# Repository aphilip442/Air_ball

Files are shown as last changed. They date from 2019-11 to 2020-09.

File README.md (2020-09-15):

# Air_ball

Describes how to make a 3D printed air ball holder with mouse sensors to capture the ball's motion. 

Can be used in behavioral rigs with mice.

Demo CountPages airball (https://www.youtube.com/watch?v=CR8DfGOpQPQ)

## Parts

* 3D printed parts: bottom and top
* M6 thread heat-insert: https://befr.rs-online.com/web/p/threaded-inserts/0278629/
* M4 thread heat-insert: https://befr.rs-online.com/web/p/threaded-inserts/0278607/
* M6 pneumatic push-in fitting: https://befr.rs-online.com/web/p/pneumatic-straight-fittings/1216041/
* Pressure regulator : SMC pneumatics - Model: ARM11A B3-208-J1: 
https://www.smc.eu/portal_ssl/WebContent/digital_catalog_2/jsp/view_product_configurator.jsp?dc_product_id=87018&part_number=ARM11AB3-508-J1
* 6mm tubing: https://www.smc.eu/portal_ssl/WebContent/digital_catalog_2/jsp/view_product_configurator.jsp?dc_product_id=54694&lang=fr&ctry=BE
* Warning: this assumes you have a source for pressured air

## How to assemble

* 3D print the components (black PLA)
* Heat-insert M4-M6 threads in the 3D parts with a soldering iron
* Put an M6 push-in fitting in the only hole that goes through the plastic
* Use epoxy to glue bottom and top parts

# Motion Sensors 
## Parts

* 2x 3D printed parts: sensor holder 
* 2x Motion sensor PMW3360: https://www.tindie.com/products/jkicklighter/pmw3360-motion-sensor/
* 2x Arduino Micro
* 1x Arduino Due
* 1x PCB

## Power

Both board types take 12V on Vin and share the same GND.

## How to connect sensors to Micros

Pinout Sensor - Micro:
-------
* RS --- (NONE)
* GD --- GND
* MT --- Pin 7 (PE6, INT6) -> movement interrupt
* SS --- Pin 10 (PB6)
* SC --- SCK (PB1)
* MO --- MOSI (PB2)
* MI --- MISO (PB3)
* VI --- 5V

https://www.tindie.com/products/jkicklighter/pmw3360-motion-sensor/

## How to connect Micros to Due

We are using the serial ports and the Due provides power.

WARNING: the Due works on 3.3V and the Micros on 5V.

Pinout Due - Micro
-------
* RX  = voltage divider from TX (5V(micro)->3.3V(due), use 2k and 1k resistors)

# Micro's output

XY motion from the sensor, sampled at around 1kHz

# Due's output

Yaw - pitch - roll values (you can add eventual other outputs like the total distance)

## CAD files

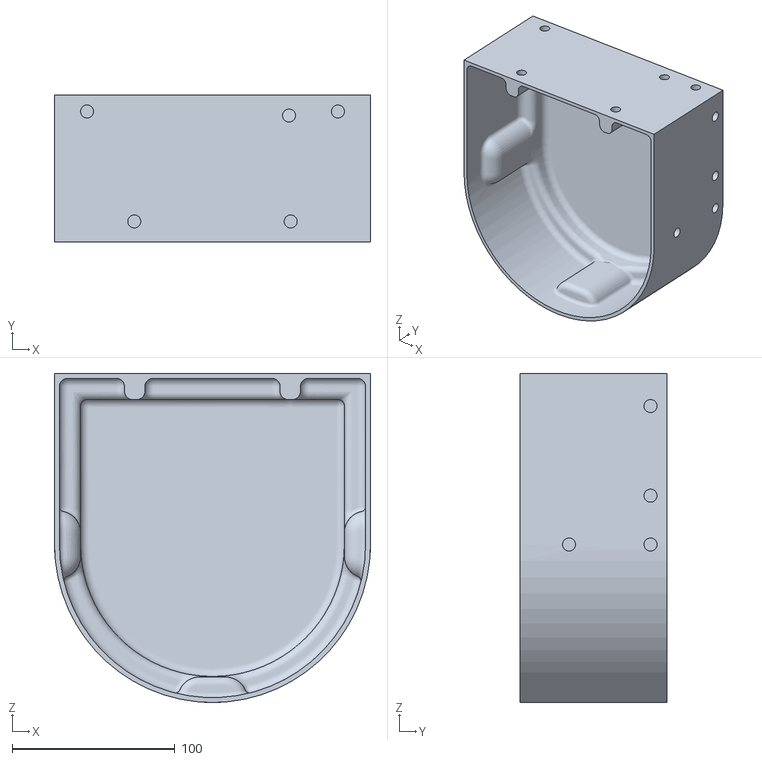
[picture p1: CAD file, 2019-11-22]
cad_files/air_ball_bottom.STL
194.0 x 90.0 x 202.0

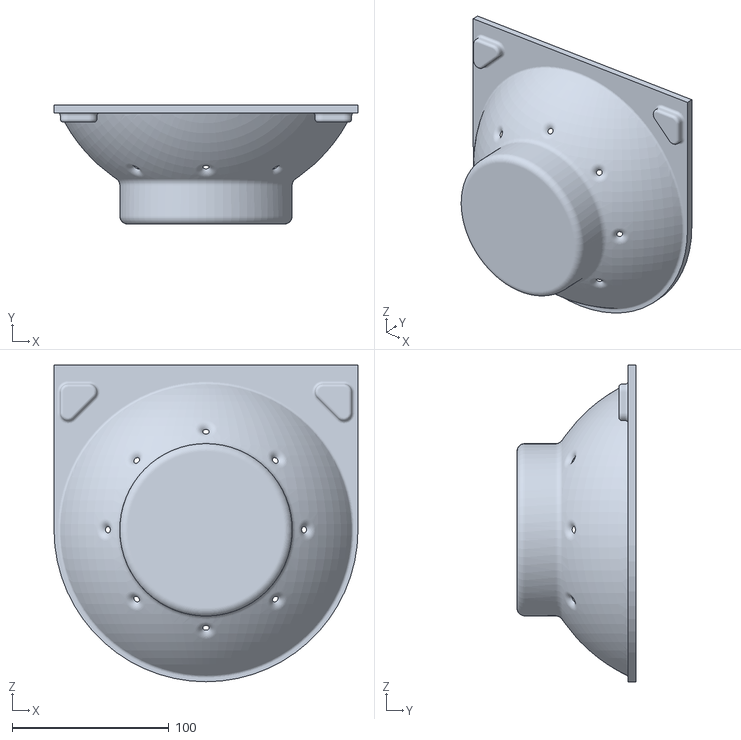
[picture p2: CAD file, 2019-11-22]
cad_files/air_ball_top.STL
194.0 x 76.0 x 202.0

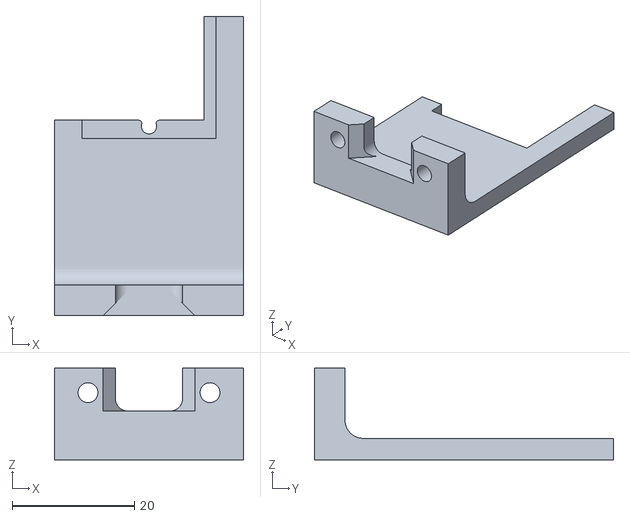
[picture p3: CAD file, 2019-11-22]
cad_files/sensor_holder.STL
31.0 x 49.0 x 15.0

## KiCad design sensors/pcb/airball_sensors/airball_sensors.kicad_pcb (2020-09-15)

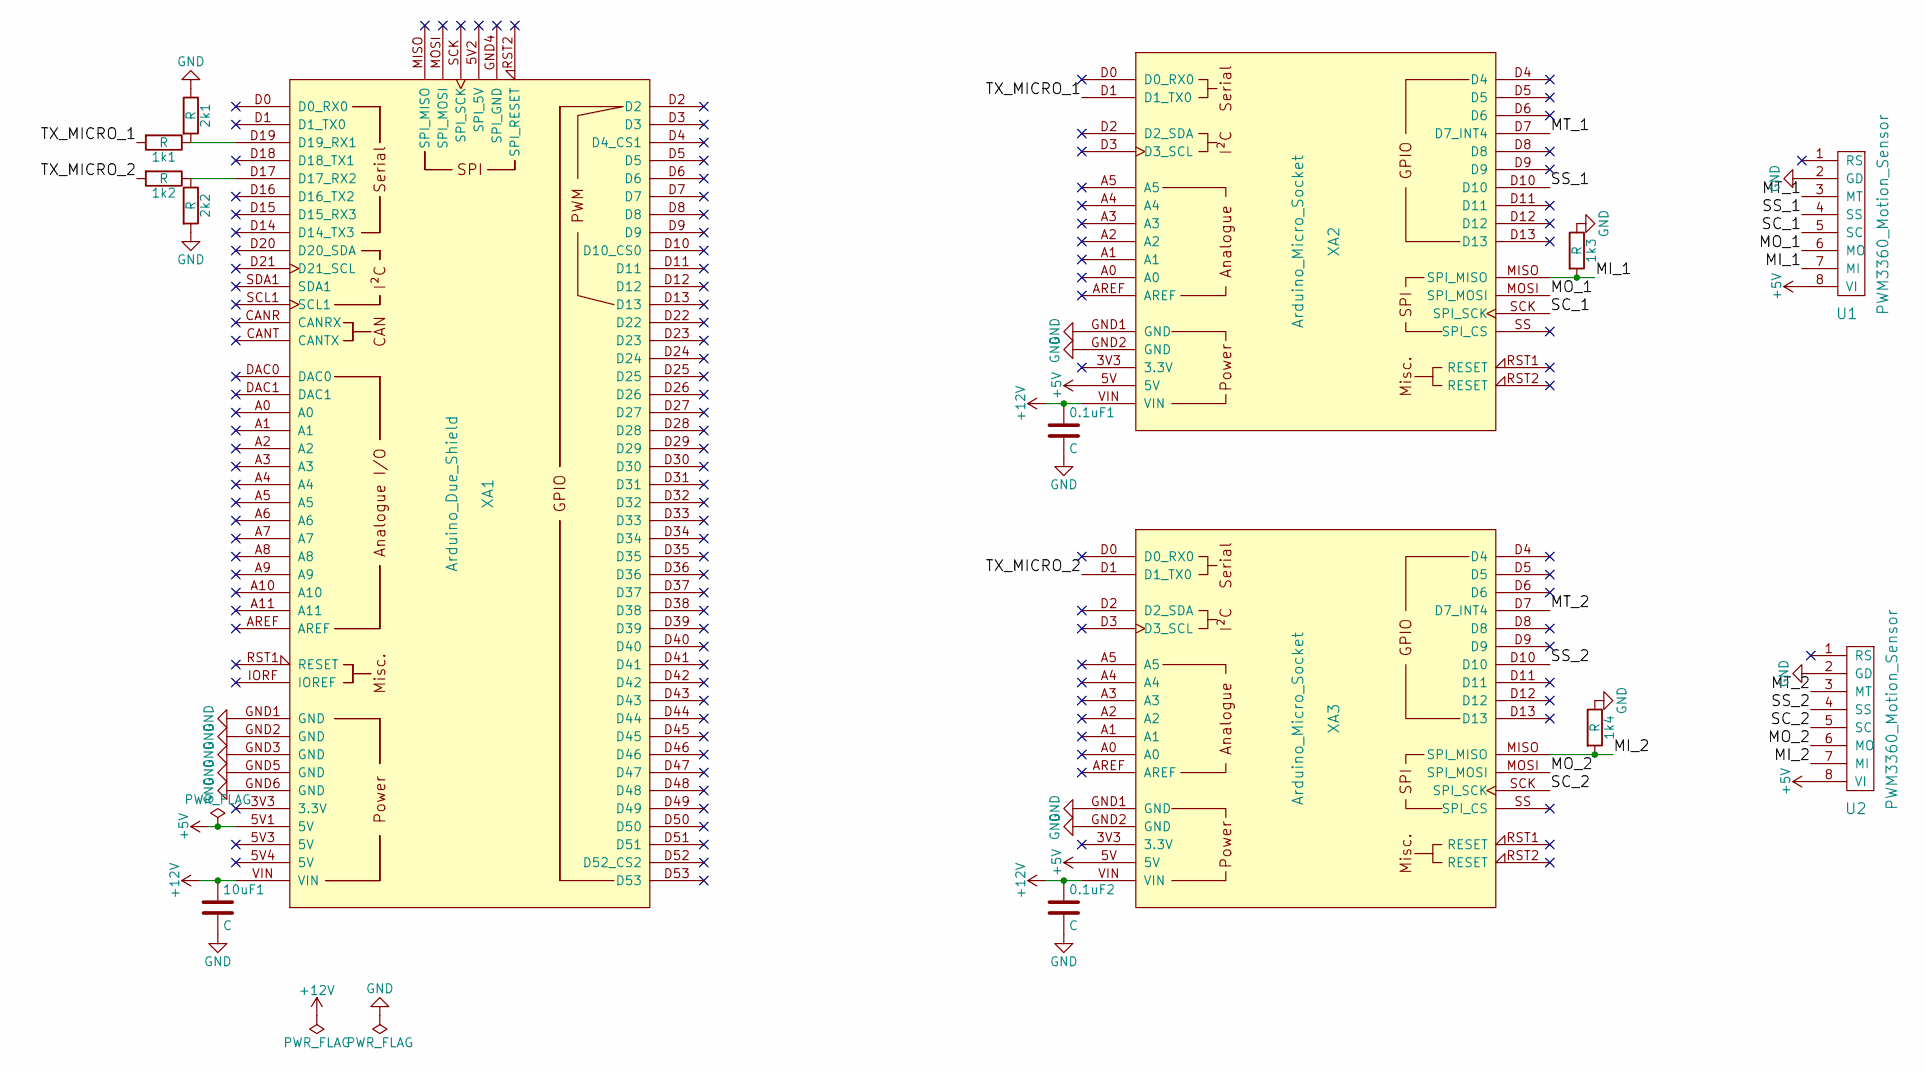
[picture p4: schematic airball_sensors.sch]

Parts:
0.1uF1, 0.1uF2, 10uF1: C; C_Disc_D6.0mm_W2.5mm_P5.00mm
1k1, 1k2, 1k3, 1k4, 2k1, 2k2: R; R_Axial_DIN0207_L6.3mm_D2.5mm_P7.62mm_Horizontal
U1, U2: PWM3360_Motion_Sensor; Socket_Strip_Angled_1x08_Pitch2.54mm
XA1: Arduino_Due_Shield
XA2, XA3: Arduino_Micro_Socket

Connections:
+5V: U1.8 (VI), U2.8 (VI), XA1.5V1 (5V), XA2.5V, XA3.5V
+12V: 0.1uF1.1, 0.1uF2.1, 10uF1.1, XA1.VIN, XA2.VIN, XA3.VIN
/MI_1: 1k3.2, U1.7 (MI), XA2.MISO (SPI_MISO)
/MI_2: 1k4.2, U2.7 (MI), XA3.MISO (SPI_MISO)
/MO_1: U1.6 (MO), XA2.MOSI (SPI_MOSI)
/MO_2: U2.6 (MO), XA3.MOSI (SPI_MOSI)
/MT_1: U1.3 (MT), XA2.D7 (D7_INT4)
/MT_2: U2.3 (MT), XA3.D7 (D7_INT4)
/SC_1: U1.5 (SC), XA2.SCK (SPI_SCK)
/SC_2: U2.5 (SC), XA3.SCK (SPI_SCK)
/SS_1: U1.4 (SS), XA2.D10
/SS_2: U2.4 (SS), XA3.D10
/TX_MICRO_1: 1k1.2, XA2.D1 (D1_TX0)
/TX_MICRO_2: 1k2.2, XA3.D1 (D1_TX0)
GND: 0.1uF1.2, 0.1uF2.2, 1k3.1, 1k4.1, 2k1.1, 2k2.2, 10uF1.2, U1.2 (GD), U2.2 (GD), XA1.GND1 (GND), XA1.GND2 (GND), XA1.GND3 (GND), XA1.GND5 (GND), XA1.GND6 (GND), XA2.GND1 (GND), XA2.GND2 (GND), XA3.GND1 (GND), XA3.GND2 (GND)
unnamed: 1k1.1, 2k1.2, XA1.D19 (D19_RX1)
unnamed: 1k2.1, 2k2.1, XA1.D17 (D17_RX2)

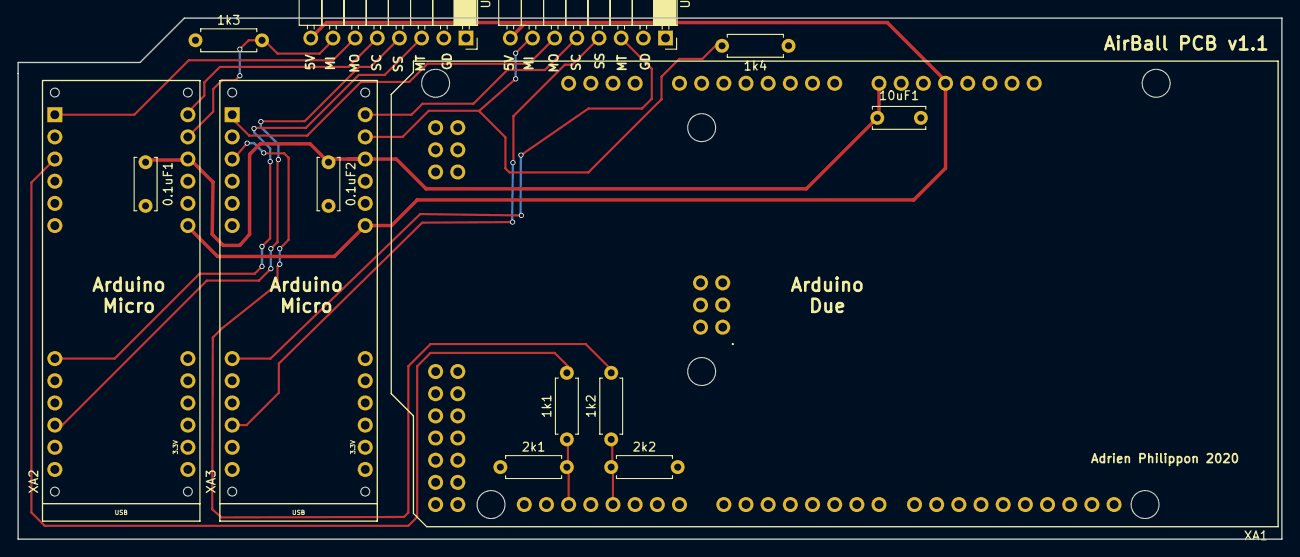
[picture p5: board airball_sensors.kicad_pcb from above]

Board: 2 copper layers, 144.8 x 59.7 mm, 14 parts (0 on the bottom side), 17 nets.

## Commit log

2019-11-24 Added PCB layout
    [airball_sensors.kicad_pcb]
2020-09-15 reorganized folder
    [airball_sensors.kicad_pcb, airball_sensors.sch]
2020-09-15 PCB v1.1
    [airball_sensors.kicad_pcb, airball_sensors.sch]
